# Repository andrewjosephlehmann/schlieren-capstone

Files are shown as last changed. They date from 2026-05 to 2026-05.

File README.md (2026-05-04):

# schlieren-capstone

Warning:

This experiment involves a high power draw (up to 320 watts total); the initial apparatus can only handle 40 watts due to inadequate bus wiring and a power supply. (Do not run the apparatus continuously, as it would be prone to an electrical fire if a hardware malfunction were to occur due to jumper connectors employed as the bus bar)). To reduce the risk of electric shock, do not touch the water in the fish tank while the apparatus is powered on. 

BOM: 

* Electrical:
  - 1 x 8 relay module: https://a.co/d/0czdi1bT 
  - 8 x 40W 12V heater cartridges: https://a.co/d/03P65jwe
  - 8 x NTC 3950 thermistors: https://a.co/d/0iHnboFi
  - 1 x Arduino Leonardo: https://store-usa.arduino.cc/products/arduino-leonardo-with-headers?srsltid=AfmBOoopEuwnMk43cNNV7SrJ7226z1KlUBDf1nWerPvuCSxlYED7YSE5

  - 1 x Sparkfun PID 13906 https://a.co/d/0bEcR1Cd
  - 1 x 120W 12v 10A power supply

* Structual:
  - 1 x Marine Epoxy (maximum rated temperature is 93C)
  - 1 x Heater holder (found in 3D models folder, constructed with ABS at 100% infill)

Experimental Setup:

Follow the same procedure for the heat gun test as outlined in the Scheliren capstone manual to ensure the camera can detect optical inhomogeneities emanating from the heat gun. 

Ensure the heater array is inserted into the water upright, as shown in the image below:

14EA9531-E6D1-43EA-80B7-8CA05D96342D_1_105_c

The apparatus was initially held upright with a clamp, as shown in this image:

E06C874C-9FB6-4DA0-A63A-565C320C115C_1_105_c

If the heater array is not redesigned so that the heater and temperature-sensor wires do not compromise its stability while upright, use a clamp made of a non-corrosive material, such as plastic. Otherwise, the water quality may degrade rapidly, obstructing the optical setup’s ability to observe inhomogeneities in the water.

If this is replicated in the future, I would strongly recommend organizing the cables to prevent tangling, which could tug on the heater or temperature sensor wires. 

Software:

The array of heaters was controlled with the control.py program listed in the repository. The firmware for the Arduino Leonardo uses a PID script adapted to work with relays located in the 'thermal_pid' folder.

opticalflow.py:

The Python program opticalflow.py allows one to measure the velocity of turbulent patterns from .wmv files already provided in the repository. For new data, make sure to retrieve the meters-per-pixel ratio, which allows us to extrapolate the velocity of the propagating patterns in the water. I initially did this by measuring the distance from the bottom of the heater to the waterline in the video, and then, using cropping software, I obtained the number of pixels corresponding to that measured length (L/px). 

When running the Python cell, a pop-up window titled 'select ROI' will appear. This allows you to specify which part of the video to run the optical flow algorithm on. To specify the region, left-click and drag your cursor to form the bounding box, and press 'return/enter' to confirm the selection. 


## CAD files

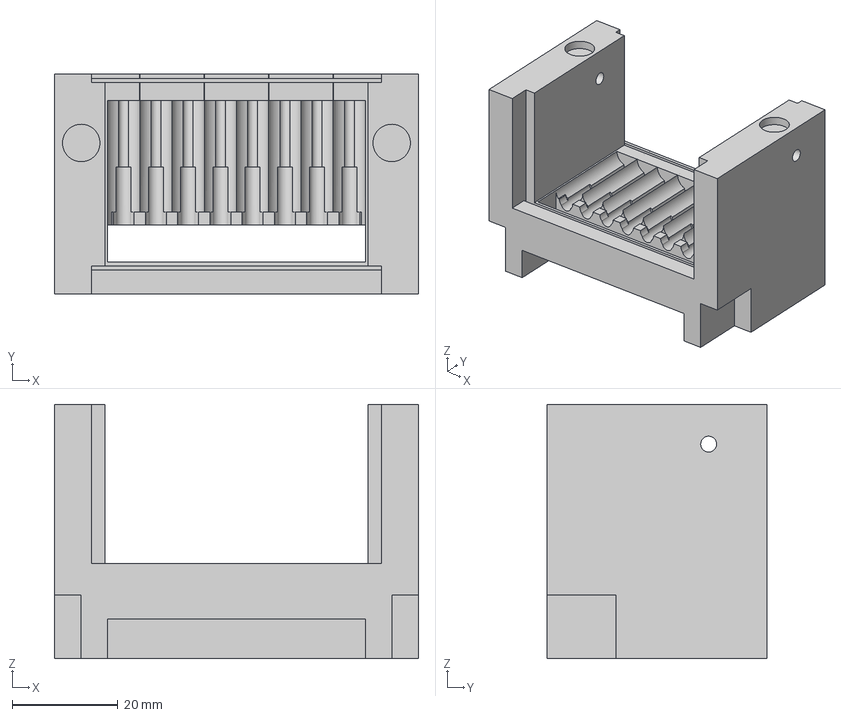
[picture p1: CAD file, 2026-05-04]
3D models/HeaterBodyWithPanelCuttouts.3mf
68.7 x 41.5 x 48.0 mm

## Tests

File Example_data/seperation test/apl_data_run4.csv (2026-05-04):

timestamp | T0 | T1 | T2 | T3 | T4 | T5 | T6 | mon1 | mon2 | State
2026-03-09T14:00:13.349842 | 27.7 | 23.6 | 21.9 | 22.3 | 24.6 | 21.9 | 21.4 | 21.1 | 25.0 | -1
2026-03-09T14:00:13.364898 | 26.4 | 23.3 | 21.9 | 22.3 | 23.5 | 21.9 | 21.3 | 21.2 | 24.3 | 0
2026-03-09T14:00:13.377803 | 27.5 | 23.5 | 21.9 | 22.3 | 24.5 | 21.9 | 21.3 | 21.2 | 25.7 | 0
2026-03-09T14:00:13.388990 | 26.6 | 23.4 | 22.0 | 22.4 | 23.5 | 21.9 | 21.3 | 21.1 | 24.0 | 0
2026-03-09T14:00:13.401959 | 27.4 | 23.6 | 22.0 | 22.4 | 24.6 | 21.9 | 21.3 | 21.2 | 27.4 | 0
2026-03-09T14:00:13.416036 | 26.8 | 23.5 | 22.0 | 22.4 | 23.2 | 21.9 | 21.3 | 21.1 | 23.6 | 0
2026-03-09T14:00:13.427480 | 27.4 | 23.5 | 22.0 | 22.3 | 23.8 | 21.9 | 21.3 | 21.1 | 27.3 | 0
2026-03-09T14:00:13.439143 | 27.4 | 23.5 | 21.9 | 22.4 | 23.3 | 21.8 | 21.4 | 21.1 | 22.6 | 0
2026-03-09T14:00:13.452081 | 27.4 | 23.4 | 22.0 | 22.3 | 23.9 | 21.9 | 21.2 | 21.1 | 25.6 | 0
2026-03-09T14:00:13.464522 | 28.0 | 23.6 | 22.0 | 22.4 | 23.4 | 21.9 | 21.4 | 21.1 | 22.3 | 0
2026-03-09T14:00:13.476425 | 27.2 | 23.4 | 22.0 | 22.4 | 23.7 | 21.9 | 21.2 | 21.1 | 24.7 | 0
2026-03-09T14:00:13.492422 | 28.7 | 23.6 | 22.0 | 22.4 | 23.9 | 21.8 | 21.4 | 21.1 | 22.4 | 0
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

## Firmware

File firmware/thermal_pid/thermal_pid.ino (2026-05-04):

#include <PID_v1.h>

/////////////////////
// Pin Definitions //
/////////////////////

const int selectPins[3] = {11, 12, 10};
const int zInput = A0;

const int extmon1 = A1;
const int extmon2 = A2;


const int relayPins[7]   = {2, 3, 4, 5, 6, 7, 8};
const int muxChannels[7] = {0, 2, 4, 3, 5, 6, 7};

const int RELAY_ON  = LOW;
const int RELAY_OFF = HIGH;

/////////////////////
// Thermistor
/////////////////////

const float SERIES_RESISTOR    = 100000.0;
const float NOMINAL_RESISTANCE = 100000.0;
const float NOMINAL_TEMP       = 25.0;
const float B_COEFFICIENT      = 3950.0;

/////////////////////
// PID
/////////////////////

double Setpoint[7];
double Input[7];
double Output[7];


// External thermistors // 
double mon1;
double mon2;

double Kp = 1;
double Ki = 0.5;
double Kd = 0;

PID pid[7] = {
  PID(&Input[0], &Output[0], &Setpoint[0], Kp, Ki, Kd, DIRECT),
  PID(&Input[1], &Output[1], &Setpoint[1], Kp, Ki, Kd, DIRECT),
  PID(&Input[2], &Output[2], &Setpoint[2], Kp, Ki, Kd, DIRECT),
  PID(&Input[3], &Output[3], &Setpoint[3], Kp, Ki, Kd, DIRECT),
  PID(&Input[4], &Output[4], &Setpoint[4], Kp, Ki, Kd, DIRECT),
  PID(&Input[5], &Output[5], &Setpoint[5], Kp, Ki, Kd, DIRECT),
  PID(&Input[6], &Output[6], &Setpoint[6], Kp, Ki, Kd, DIRECT)
};

/////////////////////
// Timing
/////////////////////

const int WindowSize = 1000;
unsigned long windowStartTime;

/////////////////////
// Serial Buffer
/////////////////////

#define CMD_BUFFER 40
char commandBuffer[CMD_BUFFER];
byte commandIndex = 0;

/////////////////////
// Setup
/////////////////////

void setup() {

  Serial.begin(9600);

  windowStartTime = millis();

  for (int i = 0; i < 3; i++) {
    pinMode(selectPins[i], OUTPUT);
    digitalWrite(selectPins[i], LOW);
  }

  pinMode(zInput, INPUT);

  for (int i = 0; i < 7; i++) {
    pinMode(relayPins[i], OUTPUT);
    digitalWrite(relayPins[i], RELAY_OFF);

    Setpoint[i] = 0.0;

    pid[i].SetOutputLimits(0, WindowSize);
    pid[i].SetSampleTime(1000);
    pid[i].SetMode(AUTOMATIC);
  }

}

/////////////////////
// Main Loop
/////////////////////

void loop() {

  readSerialCommands();

  // Read sensors
  for (int i = 0; i < 7; i++) {
    Input[i] = readThermistor(muxChannels[i]);
  }

  mon1 = readThermistorDirect(extmon1);
  mon2 = readThermistorDirect(extmon2);
  
  // Compute PID
  for (int i = 0; i < 7; i++) {
    pid[i].Compute();
  }

  // Update window
  unsigned long now = millis();
  if (now - windowStartTime > WindowSize) {
    windowStartTime += WindowSize;
  }
  unsigned long elapsed = now - windowStartTime;

  // Heater control
  for (int i = 0; i < 7; i++) {

    // Safety: shut off on invalid reading
    if (Input[i] < -50 || Input[i] > 150) {
      digitalWrite(relayPins[i], RELAY_OFF);
      continue;
    }

    // Safety: shut off if far above setpoint
    if (Input[i] > Setpoint[i] + 15) {
      digitalWrite(relayPins[i], RELAY_OFF);
      continue;
    }

    if (elapsed < Output[i]) {
      digitalWrite(relayPins[i], RELAY_ON);
    } else {
      digitalWrite(relayPins[i], RELAY_OFF);
    }

  }

  // Output temperatures
  Serial.print("DATA");
  for (int i = 0; i < 7; i++) {
  Serial.print(",");
  Serial.print(Input[i], 1);
  }
  Serial.print(",");
  Serial.print(mon1,1);
  Serial.print(",");
  Serial.print(mon2,1);

  Serial.println();

  delay(50);

}

/////////////////////
// Thermistor
/////////////////////

float readThermistor(int muxChannel) {

  selectMuxPin(muxChannel);

  analogRead(zInput);
  delayMicroseconds(50);

  int raw = analogRead(zInput);

  if (raw == 0) return -999;

  float resistance = SERIES_RESISTOR * (1023.0 / raw - 1.0);

  // Steinhart-Hart equation
  float steinhart = log(resistance / NOMINAL_RESISTANCE);
  steinhart /= B_COEFFICIENT;
  steinhart += 1.0 / (NOMINAL_TEMP + 273.15);

  return (1.0 / steinhart) - 273.15;

}

float readThermistorDirect(int analogPin) {

  int raw = analogRead(analogPin);

  if (raw == 0) return -999;

  float resistance = SERIES_RESISTOR * (1023.0 / raw - 1.0);

  float steinhart = log(resistance / NOMINAL_RESISTANCE);
  steinhart /= B_COEFFICIENT;
  steinhart += 1.0 / (NOMINAL_TEMP + 273.15);

  return (1.0 / steinhart) - 273.15;
}

void selectMuxPin(byte pin) {
  for (int i = 0; i < 3; i++) {
    digitalWrite(selectPins[i], (pin & (1 << i)) ? HIGH : LOW);
  }
}

/////////////////////
// Serial Commands
/////////////////////

void readSerialCommands() {

  while (Serial.available()) {

    char c = Serial.read();

    if (c == '\n' || c == '\r') {
      commandBuffer[commandIndex] = '\0';
      if (commandIndex > 0) {         // ignore blank lines
        parseCommand(commandBuffer);
      }
      commandIndex = 0;
    } else {
      if (commandIndex < CMD_BUFFER - 1) {
        commandBuffer[commandIndex++] = c;
      }
    }

  }

}

void parseCommand(char *cmd) {

  char *token = strtok(cmd, ",");

  if (token == NULL || strcmp(token, "SET") != 0) {
    Serial.println("ERR:CMD");
    return;
  }

  token = strtok(NULL, ",");
  if (token == NULL) {
    Serial.println("ERR:CHANNEL");
    return;
  }
  int ch = atoi(token);

  token = strtok(NULL, ",");
  if (token == NULL) {
    Serial.println("ERR:VALUE");
    return;
  }
  float sp = atof(token);

  if (ch < 0 || ch >= 7) {
    Serial.println("ERR:CHANNEL");
    return;
  }

  Setpoint[ch] = sp;

  pid[ch].SetMode(MANUAL);
  Output[ch] = 0;
  pid[ch].SetMode(AUTOMATIC);

  Serial.print("SETPOINT ");
  Serial.print(ch);
  Serial.print(" -> ");
  Serial.println(sp);

}

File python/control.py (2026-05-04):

# %%
''' 
Preliminary control program for modulating the surface temperature
of the eight heaters. Note that one of them are currently disabled due to short on one 
of the thermistors.

Author: Andrew Lehmann




'''


import serial
import time
import csv
import math
from datetime import datetime

############################
# Configuration
############################

PORT = "/dev/cu.usbmodem1301"  # on windows, this may be assigned to COM ports    
BAUD = 9600

NUM_HEATERS = 7
NUM_TEMPS = 9              # 7 heater thermistors + 2 external monitors (mon1, mon2)
COMMAND_INTERVAL = 1.0     # seconds between setpoint updates
LOGFILE = "0.1s_40s.csv"


MAX_SAFE_TEMP = 93.0

############################
# Experiment Generators
############################

def generate_temp_sweep(target_heater, start_temp, end_temp, step, hold_time_s):
    """
    Experiment 1: Power vs. Instability
    Gradually steps up the temperature on a single heater to find the transition height (hc).
    """
    schedule = []
    current_time = 0
    current_temp = start_temp

    while current_temp <= end_temp:
        schedule.append((current_time, current_time + hold_time_s, {target_heater: current_temp}))
        current_time += hold_time_s
        current_temp += step

    return schedule

def generate_spacing_sweep(fixed_heater, sweep_heaters, target_temp, hold_time_s):
    """
    Experiment 2: Multi-Plume Interference
    Keeps Heater 0 on, and sequentially turns on Heater 1, then 2, then 3...
    to test the merging height at different separation distances (r).
    """
    schedule = []
    current_time = 0

    for moving_heater in sweep_heaters:
        active_heaters = {
            fixed_heater: target_temp,
            moving_heater: target_temp
        }
        schedule.append((current_time, current_time + hold_time_s, active_heaters))
        current_time += hold_time_s

    return schedule

def phase_difference(heater1, heater2, target_temp, delay_s, hold_time_s, iterations=1):
    """
    Experiment 3: Fire heater1, then heater2 after delay_s.
    Both run together for the remainder of hold_time_s.
    Repeats for 'iterations' cycles with both heaters off between cycles.
    """
    schedule = []
    current_time = 0

    for _ in range(iterations):
        # Phase A: heater1 only
        schedule.append((current_time, current_time + delay_s, {heater1: target_temp}))
        
        # Phase B: both heaters together for remaining hold time
        schedule.append((current_time + delay_s, current_time + hold_time_s, {
            heater1: target_temp,
            heater2: target_temp
        }))
        
        # Cool-down gap between iterations (equal to hold_time_s)
        current_time += hold_time_s + hold_time_s

    return schedule

############################
# Schedule Setup
############################

# Choose WHICH experiment to run by uncommenting one of these:

# --- Experiment 1: Temp Sweep on Heater 3 (30C to 70C in 5C steps, 60s hold each) ---
# schedule = generate_temp_sweep(target_heater=3, start_temp=30, end_temp=90, step=5, hold_time_s=150)

# --- Experiment 2: Keep Heater 0 at 60C, test spacing by enabling H1..H6 for 90s each ---
#schedule = generate_spacing_sweep(fixed_heater=1, sweep_heaters=[2,3,4,5,6], target_temp=90, hold_time_s=150)


schedule = phase_difference(heater1=1, heater2=2, target_temp=90, delay_s=0.2, hold_time_s=40, iterations=1)

############################
# Serial & Logging Setup
############################

ser = serial.Serial(PORT, BAUD, timeout=1)
time.sleep(2)  # Wait for Arduino to reset after serial connect

logfile = open(LOGFILE, "w", newline="")
writer = csv.writer(logfile)
writer.writerow(["timestamp", "T0", "T1", "T2", "T3", "T4", "T5", "T6", "mon1", "mon2", "State"])

############################
# Controller Functions
############################

def set_temp(channel, temp):
    """Send a SET command to the Arduino. Uses CRLF and flushes immediately."""
    cmd = f"SET,{channel},{temp}\r\n"      
    print(f"  >> Sending: {cmd.strip()}")   
    ser.write(cmd.encode())
    ser.flush()                           

def read_line():
    """Read one line from serial. Handles disconnect and garbled bytes gracefully."""
    try:
        return ser.readline().decode().strip()
    except serial.SerialException as e:     #
        print(f"Serial error: {e}")
        return ""
    except UnicodeDecodeError:              # skip garbled bytes silently
        return ""

############################
# Safety
############################

def safety_check(temps):
    for t in temps:
        try:
            val = float(t)
            if val < -10 or val > MAX_SAFE_TEMP:
                return False
        except ValueError:
            return False  # Drop out if thermistor reads garbage/disconnects
    return True

############################
# Main Control Loop
############################

print("APL Automated Controller Started")
print(f"Safety limit: max {MAX_SAFE_TEMP}°C")

start_time = time.time()
last_command = 0
current_phase_index = -1
last_sent_setpoints = {}   

while True:
    line = read_line()

    if line.startswith("DATA"):
        parts = line.split(",")
        temps = parts[1:]
        timestamp = datetime.now().isoformat()

        if len(temps) != NUM_TEMPS:
            print(f"  [WARN] Skipping malformed line (got {len(temps)} temps, expected {NUM_TEMPS}): {line}")
            continue

        heater_temps = temps[:NUM_HEATERS]   
        writer.writerow([timestamp] + temps + [current_phase_index])
        logfile.flush()  # ensure data hits disk even if we crash
        print(f"{timestamp}  temps={temps}  phase={current_phase_index}")

        if not safety_check(heater_temps):
            print("\n!!! THERMAL RUNAWAY OR THERMISTOR DISCONNECT DETECTED !!!")
            print("SAFETY SHUTDOWN ENGAGED.")
            for i in range(NUM_HEATERS):
                if last_sent_setpoints.get(i) != 0:
                    set_temp(i, 0)
            break

    now = time.time()
    elapsed = now - start_time



    if now - last_command > COMMAND_INTERVAL:

        active_phase_found = False

        for idx, entry in enumerate(schedule):
            start, end, target_dict = entry

            if start <= elapsed <= end:
                active_phase_found = True

                if current_phase_index != idx:
                    print(f"\n--- [T={int(elapsed)}s] STARTING PHASE {idx} ---")
                    print(f"--- TARGETS: {target_dict} ---")
                    current_phase_index = idx

                for ch in range(NUM_HEATERS):
                    target = target_dict.get(ch, 0)  # 0 if not in dict (heater off)
                    if last_sent_setpoints.get(ch) != target:
                        set_temp(ch, target)
                        last_sent_setpoints[ch] = target

        if not active_phase_found and elapsed > schedule[-1][1]:
            print("\n--- EXPERIMENT COMPLETE ---")
            for i in range(NUM_HEATERS):
                if last_sent_setpoints.get(i) != 0:
                    set_temp(i, 0)
            break

        last_command = now

    time.sleep(0.01)

logfile.close()
ser.close()
print("Controller shut down cleanly.")
# %%

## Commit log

2026-05-04 Update README with safety warnings and setup details
    Added warnings about power draw and safety precautions. Expanded experimental setup details and provided recommendations for future replication. Clarified usage instructions for opticalflow.py.
2026-05-04 Update README with new BOM item and setup instructions
    Added a 120W power supply to the BOM and updated the experimental setup instructions.
2026-05-04 Add example data, control and opticalflow scripts
    Add example dataset and analysis/control code for the APL heater experiments. Files added include Example_data/python/control.py (serial heater controller with scheduling, safety checks and CSV loggi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
    [apl_data_run4.csv]
2026-05-04 Improve clarity of heater array stability instructions
    Rephrase instructions for heater array stability and clamp material.
2026-05-04 Add 3D model and macOS .DS_Store files
    Add HeaterBodyWithPanelCuttouts.3mf under '3D models' and add/update .DS_Store metadata files at the repository root and in firmware/.DS_Store are macOS Finder metadata; consider adding .DS_Store to 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
    [HeaterBodyWithPanelCuttouts.3mf]
2026-05-04 Fix typo in heater holder material description
